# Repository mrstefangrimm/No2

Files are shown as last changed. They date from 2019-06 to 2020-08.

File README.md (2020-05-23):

# Liver Deformation X-Ray Imaging Phantom
No2 (working title) is a motion phantom with 3 motion axes which are controlled independently for both linear and rotary motion.

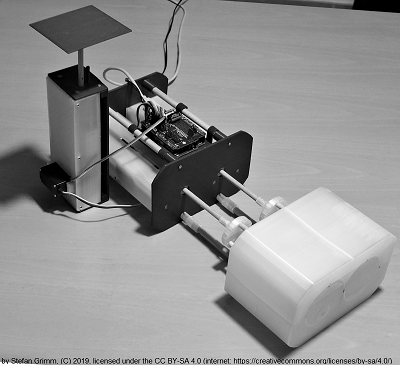
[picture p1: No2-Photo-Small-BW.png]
No2 Motion Phantom


A [video on youtube](https://youtu.be/QqYBeX8754M) shows how the phantom works.

## Project History
The project was launched in 2019. In 2020, the software for the phantom has been moved out of this project.

## Construction

A detailed description how to build this phantom is published on *[Instructables.com](https://www.instructables.com/id/Liver-Deformation-X-Ray-Imaging-Phantom/)*.

## Manufacturing Tool Chain

Software | License 
---- | -------
SketchUp | SketchUp Shop 
Ultimaker Cura | GPL

## License


This work is licensed under the Creative Commons Attribution-ShareAlike 4.0 International License. To view a copy of this license, visit http://creativecommons.org/licenses/by-sa/4.0/ or send a letter to Creative Commons, PO Box 1866, Mountain View, CA 94042, USA.

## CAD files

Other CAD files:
Instructable/SketchUp/Explosion-Actuator.skp
Instructable/SketchUp/Explosion-Body.skp
Instructable/SketchUp/Explosion-CylinderLeft.skp
Instructable/SketchUp/Explosion-CylinderRight.skp
Instructable/SketchUp/Explosion-Gating.skp
MechanicalDesign/SketchUp/No2-Back.skp
MechanicalDesign/SketchUp/No2-Body.skp
MechanicalDesign/SketchUp/No2-BodyInsertBack.skp
MechanicalDesign/SketchUp/No2-BodyInsertCenter.skp
MechanicalDesign/SketchUp/No2-CPUPlatform.skp
MechanicalDesign/SketchUp/No2-CylinderLeft.skp
MechanicalDesign/SketchUp/No2-CylinderLeftCylinder.skp
MechanicalDesign/SketchUp/No2-CylinderLeftInsertBack.skp
MechanicalDesign/SketchUp/No2-CylinderLeftInsertCenter.skp
MechanicalDesign/SketchUp/No2-CylinderLeftMarkers.skp
MechanicalDesign/SketchUp/No2-CylinderRight.skp
MechanicalDesign/SketchUp/No2-CylinderRightCylinderBack.skp
MechanicalDesign/SketchUp/No2-CylinderRightCylinderCenter.skp
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

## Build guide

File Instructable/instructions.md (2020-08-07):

# Liver Deformation X-Ray Imaging Phantom

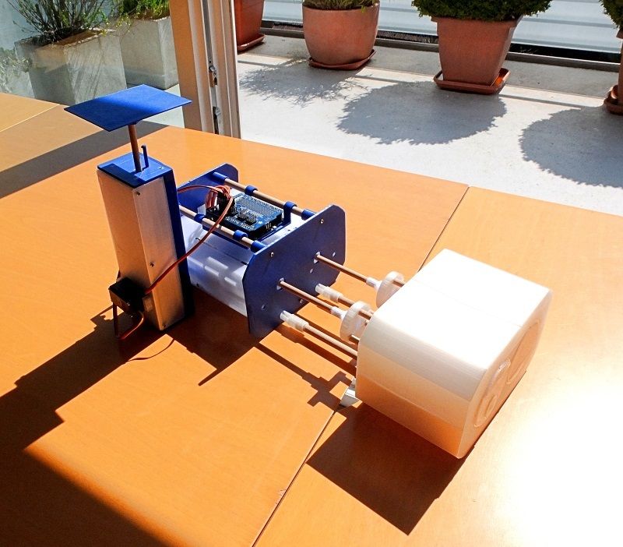
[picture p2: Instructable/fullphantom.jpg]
fullphantom


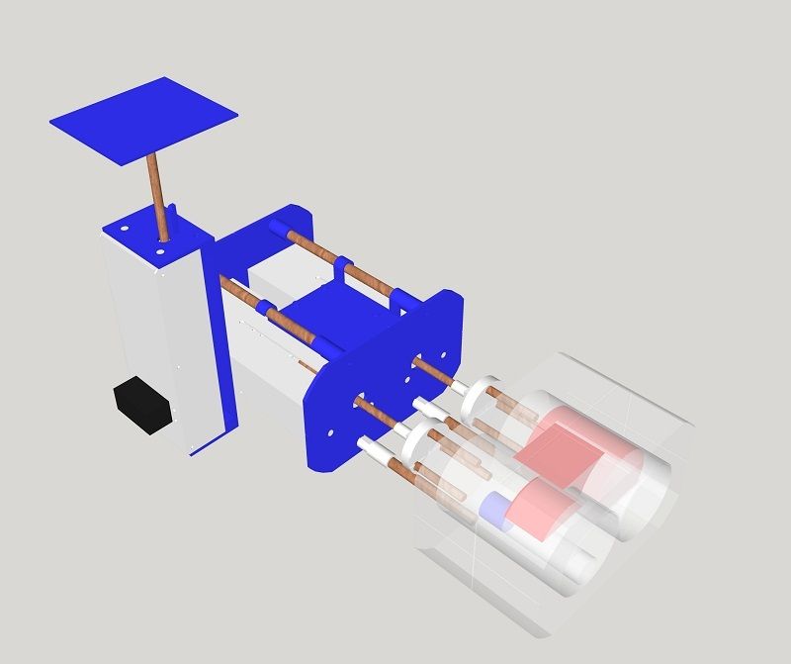
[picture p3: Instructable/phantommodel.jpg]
phantommodel


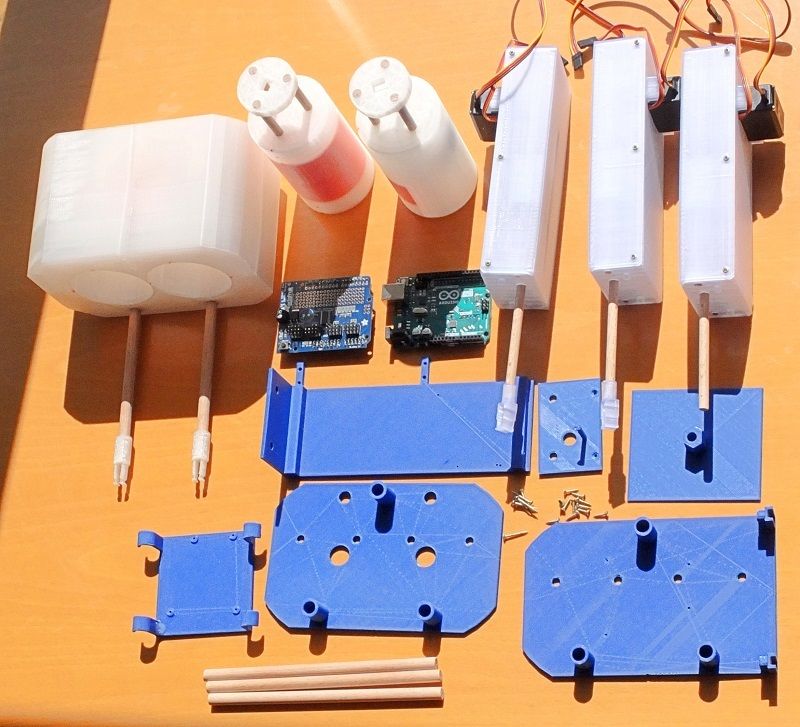
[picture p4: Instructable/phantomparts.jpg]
phantomparts


In the field of medical imaging, so called imaging phantoms are used  to evaluate, analyze, and tune the performance of various imaging  devices (Source: Wikipedia). This specially developed imaging  phantom simulates motion and deformation of a liver based on respiratory motion.

The inspiration for this project was this video on YouTube: ELPHA: Dynamically deforming liver phantom. https://youtu.be/u_GXM9yy9Ok

On an X-Ray image, the material and the density define what is a  bone, a liver or a lung. To simulate the deformation of a liver, an object of a different density than the density of the surrounding structure is needed. Different densities can also be achieved by 3D printed parts with different infill percentages. For this phantom, the printed parts that represent the liver have 60%, the part that represents the gall bladder 90% and the surrounding tissue has a 30% infill percentage.

Whereas the above mentioned ELPHA uses pressure for the deformation, this phantom simulates the  deformation by moving objects relative to each other which together represent a liver. When the left and right cylinder are moved against each other, the liver "shrinks". When the cylinders are moved in opposite direction the liver gets bigger.

This short animation gives you an idea how this phantom would look like on X-Ray images: https://youtu.be/K-1KQQ25YmM

To generate the motion, the phantom uses three [LnR-Actuators](https://www.instructables.com/id/Linear-and-Rotation-Actuator/), an Arduino micro controller and an Adafruit Servo Shield. The micro controller is  required because you cannot be in the room when you acquire X-Ray  images. The phantom can be either be remote controlled from a PC over an USB cable, or you can start one of the pre-programmed motion patterns and use the phantom stand-alone.

This phantom is suitable to evaluate and tune the performance of medical devices. A field of application could be the development of motion tracking and 4D reconstruction algorithms. Some limited imaging dosimetry should also be possible.

The direct material costs are approximately USD 200.

### Supplies:

1 Arduino Uno

1 Adafruit 16-Channel Servo Shield

3 [LnR-Actuator](https://www.instructables.com/id/Linear-and-Rotation-Actuator/)

11 Screw M2 x l10

6 Screw M2 x l20

4 Metal marker d1 x l4 mm, created from paper clip

6 Wooden dowel d6 x l40 mm

3 Wooden dowel d8 x l160 mm

2 Wooden dowel d8 x l110 mm

1 Windows PC with Java 8 runtime and .NET Framework 4.6.2

1 3D Printer

1 Standing drill is of avail

Legend: l:length, d:diameter

## Step 1: 3D Printed Parts

PLA, default 20% infill: LDXIP-Back, LDXIP-CPUPlatform, LDXIP-Flange, LDXIP-FlangeClip, LDXIP-Front, LDXIP-FrontClip, LDXIP-GatingBase, LDXIP-GatingBottom, LDXIP-GatingPlatform, LDXIP-GatingTop

PLA, 30% infill: LDXIP-Body, LDXIP-BodyInsertBack, LDXIP-CylinderLeft, LDXIP-CylinderLeftInsertBack, LDXIP-CylinderRight, LDXIP-CylinderRightCylinderBack,  LDXIP-CylinderRightInsertBack

PLA, 60% infill: LDXIP-BodyInsertCenter, LDXIP-CylinderLeftCylinder, LDXIP-CylinderLeftInsertCenter,  LDXIP-CylinderRightInsertCenter

PLA, 90% infill: LDXIP-CylinderRightCylinderCenter

## Step 2: Assemble the Two Cylinders

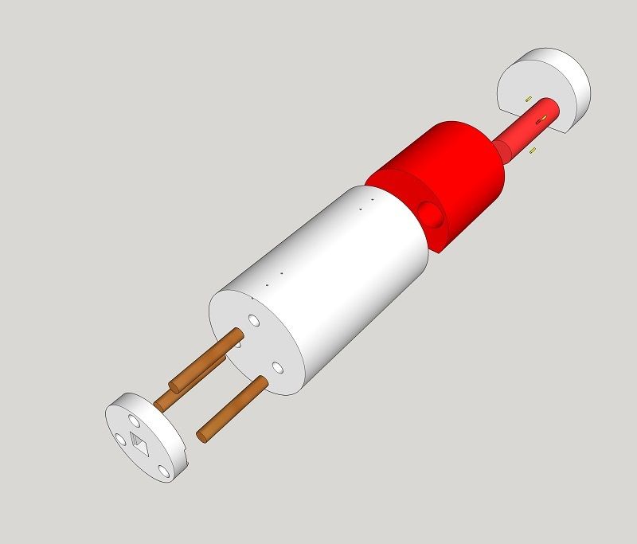
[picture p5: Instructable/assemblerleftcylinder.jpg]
assemblerleftcylinder


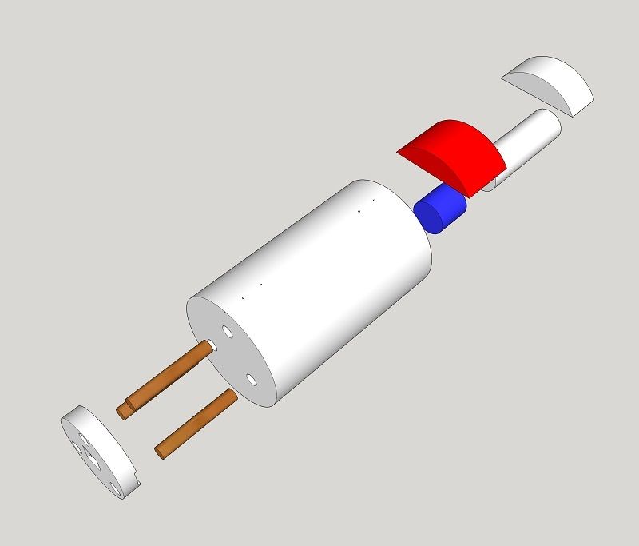
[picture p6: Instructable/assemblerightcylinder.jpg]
assemblerightcylinder


To build the left cylinder, insert the four metal markers d1 x l4 mm into the notches of the *LDXIP-CylinderLeftCylinder*. Then insert the *LDXIP-CylinderLeftCylinder* into the *LDXIP-CylinderLeftInsertCenter* and this into the *LDXIP-CylinderLeft*. Add the *LDXIP-CylinderLeftInsertBack* and fixate all the parts with a drop of glue. Insert three wooden  dowels d6 x l40 mm into the holes in the front plane of the cylinder and attach a *LDXIP-Flange*.

To build the right cylinder, insert the *LDXIP-CylinderRightInsertCenter* and add the *LDXIP-CylinderRightInsertBack*. Then insert *LDXIP-CylinderRightCylinderCenter* and *LDXIP-CylinderRightCylinderBack*. Insert three wooden dowels d6 x l40 mm into the holes in the cylinders front and attach a *LDXIP-Flange*.

## Step 3: Assemble the Phantom Body

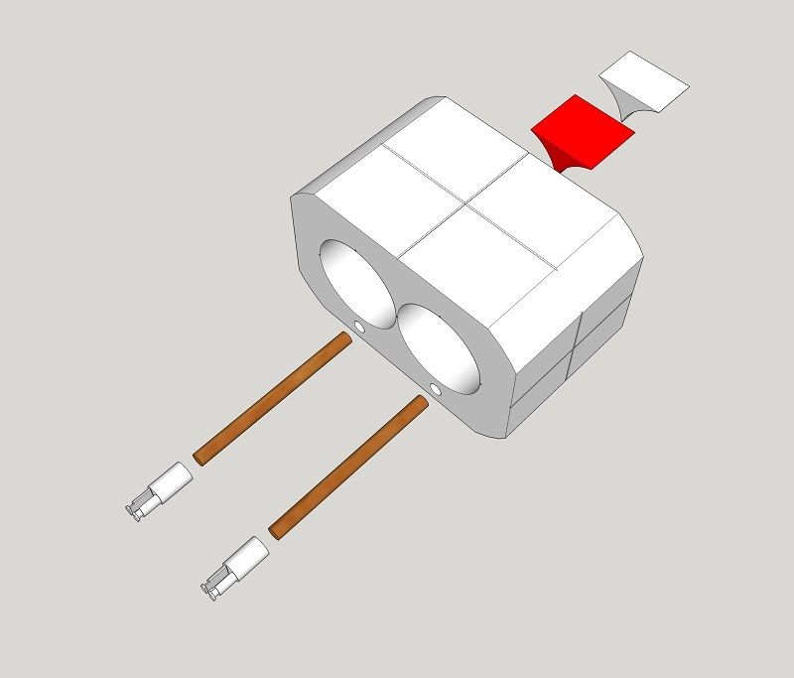
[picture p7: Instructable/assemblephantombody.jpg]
assemblephantombody


To build the body, insert the *LDXIP-BodyInsertCenter* and then the *LDXIP-BodyInsertBack* into the *LDXIP-Body*. Insert two wooden dowels d8 x l110 mm into the holes in the phantoms front and attach a *LDXIP-FrontClip.*

## Step 4: Assemble the Actuator Assembly

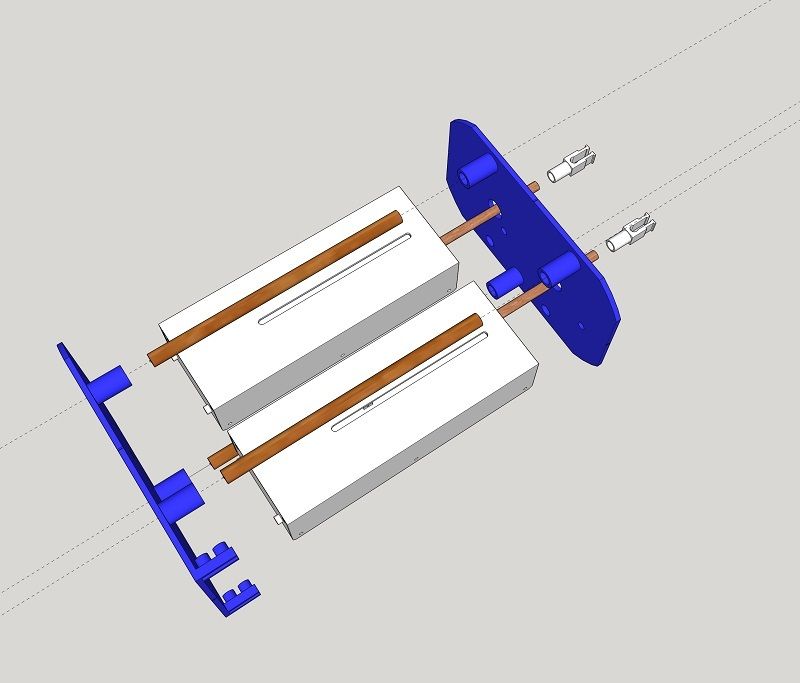
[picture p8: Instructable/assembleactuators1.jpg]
assembleactuators1


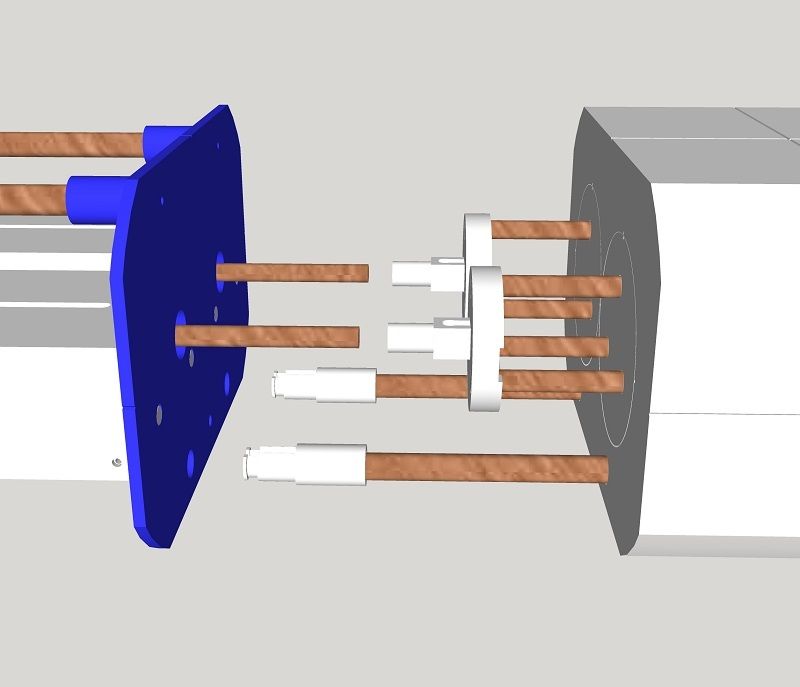
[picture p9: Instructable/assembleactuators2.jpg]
assembleactuators2


To build the actuator assembly, fixate three wooden dowels d8 x l160 mm to the *LDXIP-Back* with three screws M2 x l20 mm. Plug-in the two *LnR-Actuators* and add the *LDXIP-Front*. Add a *LDXIP-FlangeClip* to each of the LnR-Actuator shafts but do not fixate it yet.

Plug-in the assembled phantom body into the actuator assembly. Connect the  flange-clip with the flange. Align the cylinders and then fixate the  flange clips with some glue to the actuator shafts.

## Step 5: Add the Gating Platform

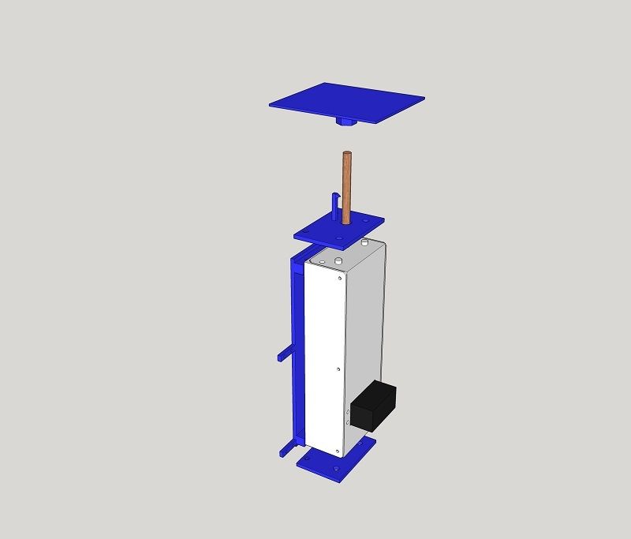
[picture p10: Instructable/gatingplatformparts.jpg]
gatingplatformparts


To build the Gating assembly, attach the *LDXIP-GatingBottom* to the *LDXIP-GatingBase* with two screws M2 x l10 mm. Plug-in a LnR-Actuator and add the *LDXIP-GatingTop*. Add the *LDXIP-GatingPlatform* and fixate it with a screw M2 x l10 mm. Attach the Gating assembly to the actuator assembly with four screws M2 x l10 mm.

## Step 6:  Add the Micro Controller

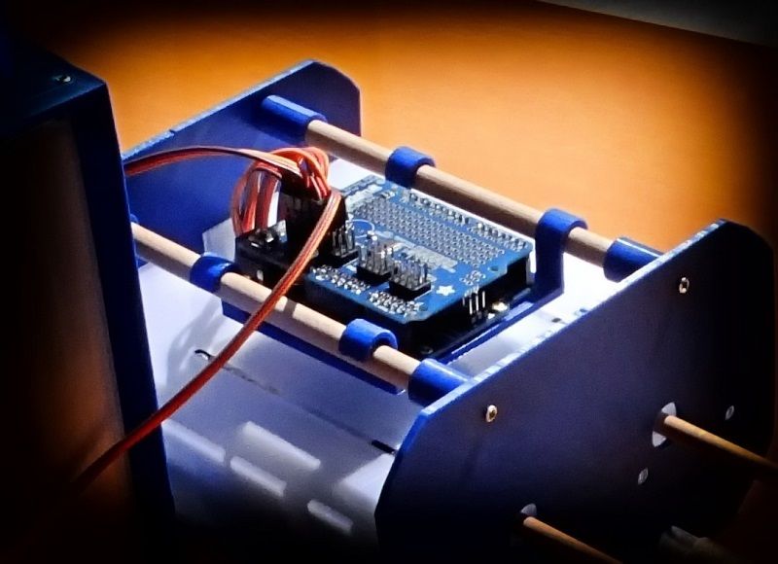
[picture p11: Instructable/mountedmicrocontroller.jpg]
mountedmicrocontroller


Mount the Arduino on the *LDXIP-CPUPlatform* and fixate it with  four screws M2 x l10 mm. Attach the Adafruit Servo Shield. Mount the CPU assembly on the actuator assembly. Connect the servos to the servo  shield in this order: Longitudinal (long cable) Left, Right, Gating.  Rotary (short cable) Left, Right, Gating.

## Step 7: Install the Firmware and Calibrate

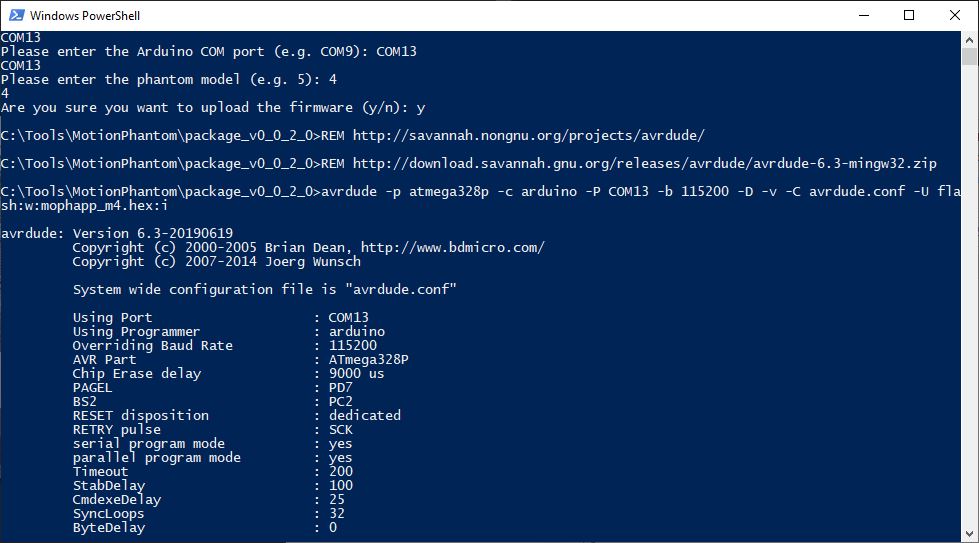
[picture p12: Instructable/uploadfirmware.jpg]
uploadfirmware


Download the package.zip (e.g. package_v0.0.2.0.zip) of the latest release from [github](https://github.com/mrstefangrimm/Phaso/releases/). The download includes the required scripts and the software to control the phantom. Unzip the package into a local folder, e.g. C:\Tools\MotionPhantom. 

Connect the phantom to your PC before the next steps.

In the download is a PowerShell script that uploads the firmware and write the calibration data to the EEPROM. To execute the script, open a PowerShell and change the directory to the target folder and then run: .\setup.ps1. Or right-click on the setup.ps1 and select Run with PowerShell.

- The script now lists one or more COM ports. Enter the phantom's port (e.g. COM13).

- For the model, enter: 4

- Confirm the firmware upload with: y

  The script uses avrdude to upload the firmware. After the upload, the firmware is active.

- Confirm the EEPROM update with: y

  The script writes the default calibration to the EEPROM.

- Confirm to run a test with: y

  The test ends with the output: Complete, and resets the firmware.

The phantom is ready for use.

## Step 8: Remote Control It With the Virtual Phantom Application

https://youtu.be/C2IkKYsVn7M

The Virtual Phantom Application is a .NET based application and part of the downloaded package (\Virms.NET\ViphApp.exe). The application simulates X-Ray imaging. And it is possible to connect and control a phantom with the application.

The program always starts with the simulation of the Marker Motion Phantom. Change the phantom on the left control panel to "Liver Phantom".

If the phantom is plugged-in, its port should in the list. Select the port and press "Connect".

On the right control panel, it is possible to either control the motion axes individually or start a program.

If you plan to write your on software: This programming interface is completely documented in this [Wiki](https://github.com/mrstefangrimm/Phaso/wiki).

## Step 9: Control It From Your Phone

https://youtu.be/yzLijWUkXsA

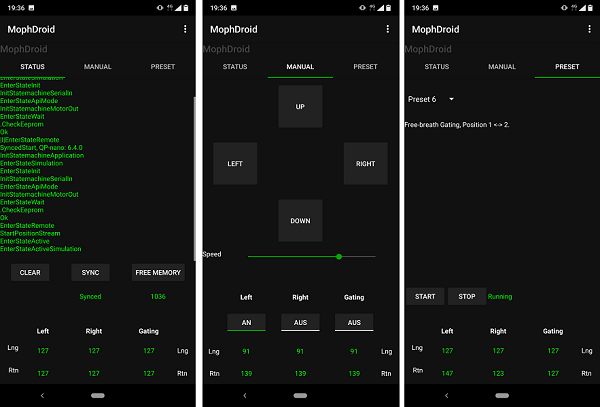
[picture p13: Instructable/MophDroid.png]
mophdroid


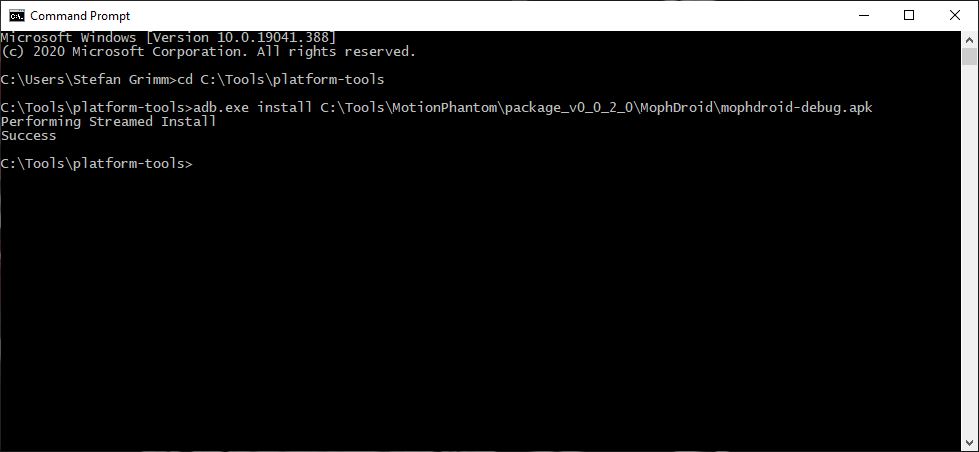
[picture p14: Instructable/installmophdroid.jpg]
installmophdroid


MophDroid is a Android App that allows you to control the phantom from your phone. This App replaces the need to every time wire your PC to the phantom. Instead you may install the App on a discarded smartphone which you then leave connected to the phantom. Like this, the phantom is always ready for use.

To install the App you have to enable the developer options on your phone. Follow [these instructions](https://www.xda-developers.com/install-adb-windows-macos-linux/) to setup your phone and your PC.

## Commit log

2019-05-12 Added SketchUp models.
    [No2-Back.skp, No2-Body.skp, No2-BodyInsertBack.skp, No2-BodyInsertCenter.skp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]
2019-05-14 Added photo. Updated SketchUp models.
    [No2-GatingScale.skp, No2-GatingTop.skp]
2019-05-25 Adapted to changed incoming serial messages for state changes (manual, preset, remote and calibration) from A-E to G-K.
2020-03-09 Replace binaries with generated binaries from Trimble.
    [No2-Back.skp, No2-Body.skp, No2-BodyInsertBack.skp, No2-BodyInsertCenter.skp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]
2020-04-12 Remove obsolete software folder and add new SketchUp models. Update Readme.
    [Explosion-Actuator.skp, Explosion-Body.skp, Explosion-CylinderLeft.skp, Explosion-CylinderRight.skp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]
2020-04-25 Removed duplicated Sketchup model Flange, FlangeClip, FrontClip and GatingPlatform.
    [No2-Flange.skp, No2-FlangeClip.skp, No2-FrontClip.skp, No2-GatingPlatform.skp]
2020-05-31 Rename folder.
    [No2-Back.skp, No2-Body.skp, No2-BodyInsertBack.skp, No2-BodyInsertCenter.skp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]
2021-08-21 Add markers Sketchup model
    [No2-CylinderLeftMarkers.skp]
